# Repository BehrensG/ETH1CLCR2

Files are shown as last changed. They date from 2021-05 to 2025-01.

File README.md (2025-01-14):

<h1>ETH1CLCR2</h1>
LCR measurement card with Ethernet interface.

<h2>PCB Design</h2>

<p align="center">3D model rendition for PCB V1.0.</p>
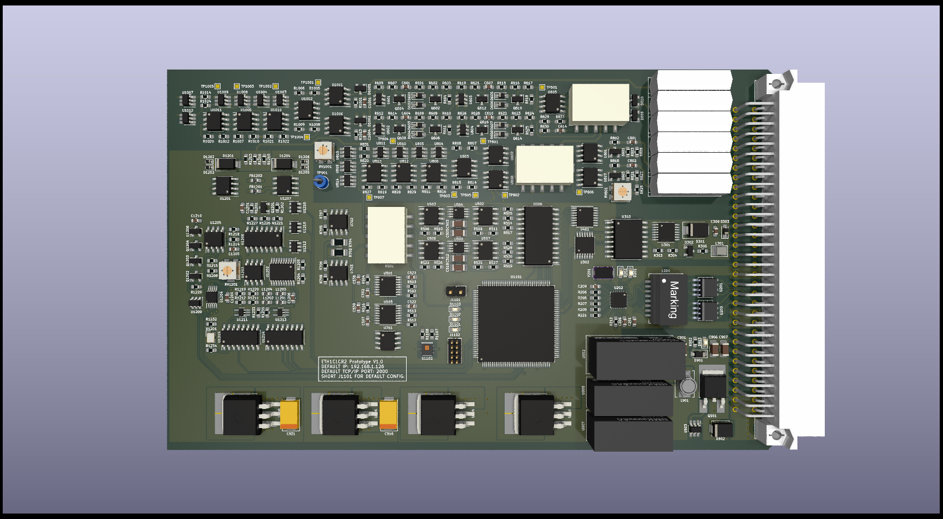
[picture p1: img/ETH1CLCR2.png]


<p align="center">Below are the images for the PCB V1.0. Mistake solved with botch wire.</p>

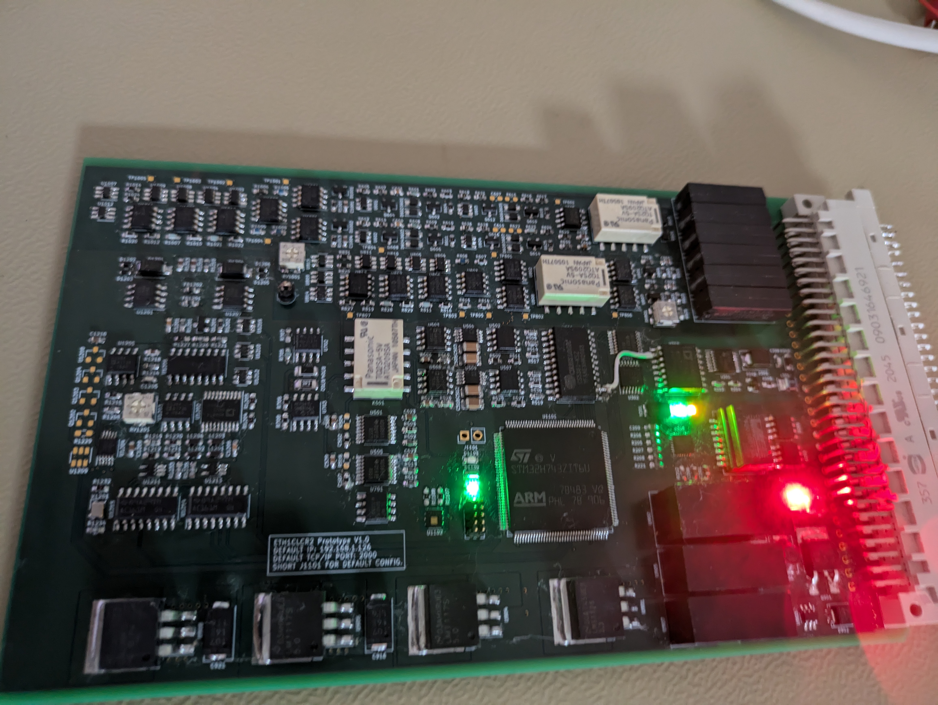
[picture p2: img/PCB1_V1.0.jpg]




<h2>Tests</h2>
Some test measurements perform on passive components. 

>[!NOTE]
>The components where measured directly, not in a circuit. The cards was not calibrated.

<table align="center">
    <tr>
        <th>Type</th>
        <th>Component</th>
        <th>Value</th>
        <th>Component Tolerance</th>
        <th>Measurement</th>
    </tr>
    <tr>
        <td>Resistor</td>
        <td>WS21R000FEK</td>
        <td>2 Ω</td>
        <td>1%</td>
        <td>2.2352 Ω</td>
    </tr>
    <tr>
        <td>Resistor</td>
        <td>SR1206JR-7W3R3L</td>
        <td>3.3 Ω</td>
        <td>5%</td>
        <td>3.8283 Ω</td>
    </tr>
    <tr>
        <td>Resistor</td>
        <td>PTF5610K000AYEK</td>
        <td>10 kΩ</td>
        <td>0.05%</td>
        <td>10.01509 kΩ</td>
    </tr>
    <tr>
        <td>Resistor</td>
        <td>RN732BTTD9002B25</td>
        <td>90 kΩ</td>
        <td>0.1%</td>
        <td>90.02021 kΩ</td>
    </tr>
    <tr>
        <td>Resistor</td>
        <td>ERA-8VRB1003V</td>
        <td>100 kΩ</td>
        <td>0.1%</td>
        <td>100.294 kΩ</td>
    </tr>
    <tr>
        <td>Resistor</td>
        <td>HHV-50FR-52-10M</td>
        <td>10 MegΩ</td>
        <td>1%</td>
        <td>10.490122 MegΩ</td>
    </tr>
    <tr>
        <td>Inductor</td>
        <td>AISR-01-104J</td>
        <td>100 mH</td>
        <td>5%</td>
        <td>102.6 mH</td>
    </tr>
    <tr>
        <td>Capacitor</td>
        <td>KP1830310061</td>
        <td>10 nF</td>
        <td>1%</td>
        <td>10.07 nF</td>
    </tr>
    <tr>
        <td>Capacitor</td>
        <td>F461BC104F400A</td>
        <td>100 nF</td>
        <td>1%</td>
        <td>106 nF</td>
    </tr>
    <tr>
        <td>Capacitor</td>
        <td>C315C101F3G5TA</td>
        <td>0.1 nF</td>
        <td>1%</td>
        <td>0.1071 nF</td>
    </tr>
    <tr>
        <td>Capacitor</td>
        <td>D83W4010M01H</td>
        <td>10 uF</td>
        <td>3%</td>
        <td>10.152 uF</td>
    </tr>
    <tr>
        <td>Capacitor</td>
        <td>MPK1839510401</td>
        <td>1 uF</td>
        <td>1%</td>
        <td>1.0695 uF</td>
    </tr>
    <tr>
        <td>Capacitor</td>
        <td>EST108M063AM3AA</td>
        <td>1 mF</td>
        <td>20%</td>
        <td>1.1 mF</td>
    </tr>
    <tr>
        <td>Capacitor</td>
        <td>F463AG102F2K0A</td>
        <td>1 nF</td>
        <td>1%</td>
        <td>1.0459 nF</td>
    </tr>
    <tr>
        <td>Capacitor</td>
        <td>MKP1839310251</td>
        <td>10 nF</td>
        <td>1%</td>
        <td>10.0974 nF</td>
    </tr>
    <tr>
        <td>Capacitor</td>
        <td>MKP1837410011</td>
        <td>100 nF</td>
        <td>1%</td>
        <td>101.457 nF</td>
    </tr>
    <tr>
        <td>Capacitor</td>
        <td>23PS222</td>
        <td>2.2 nF</td>
        <td>5%</td>
        <td>2.2161 nF</td>
    </tr>
</table>

<h2>NOTES</h2>
The ETH1CLCR2 PCB works, but I don't recommend using this design. The design has mistakes and could be made simpler and better.

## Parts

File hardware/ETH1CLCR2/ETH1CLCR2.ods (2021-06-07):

Id | Designator | Package | Quantity | Designation | Missing | Reference
1 | C1236,C1235,C1234,C1233,C536,C535,C534,C1232,C1231,C1226,C1230,C1229,C1228,C1227,C1225,C1224,C1223,C1222,C1221,C1220,C1219,C1218,C1217,C1216,C1215,C1214,C1213,C1212,C1211,C1203,C533,C532,C531,C530,C529,C528,C527,C526,C525,C524,C1121,C1120,C1119,C1118,C1117,C1116,C1115,C1114,C1113,C1112,C1111,C1110,C1109,C1108,C1107,C1105,C1019,C1018,C1015,C1014,C1013,C1012,C1011,C1016,C1010,C1017,C1009,C1008,C1007,C820,C819,C818,C813,C812,C817,C816,C815,C814,C822,C823,C811,C821,C810,C809,C808,C807,C624,C623,C622,C621,C620,C619,C618,C617,C616,C615,C612,C609,C606,C603,C523,C522,C521,C520,C308,C306,C304,C303,C301,C210,C207,C206,C205,C204,C202,C201 | C_0603_1608Metric_Pad1.08x0.95mm_HandSolder | 116 | 100n | 100
2 | C539,C538,C1210,C626,C625,C510,C1122,C1106,C1005,C1004,C1003,C1001,C805,C804,C802,C801,C704,C703,C701,C516,C514,C401,C307,C305,C302,C209,C203 | C_0603_1608Metric_Pad1.08x0.95mm_HandSolder | 27 | 1u
3 | C537,C1201,C509 | C_0603_1608Metric_Pad1.08x0.95mm_HandSolder | 3 | 10n
4 | R535,R534,R533,R532,R1230,R512,R1106,R1105,R1104,R812,R635,R627,R620,R613,R606,R513,R503,R502,R301,R220,R219,R218,R217,R213,R207 | R_0603_1608Metric_Pad0.98x0.95mm_HandSolder | 25 | 10k
5 | U1209,U1216,U1212,U1210,U604,U603,U602,U601 | SOT-23-6 | 8 | SN74LVC1T45DBV
6 | U1208 | SOT-23 | 1 | TL431DBZ | TL431IDBZR,215
7 | R1231,R1218,R1103,R1101 | R_0603_1608Metric_Pad0.98x0.95mm_HandSolder | 4 | 680 | 2
8 | R1229 | R_0603_1608Metric_Pad0.98x0.95mm_HandSolder | 1 | 51
9 | Q1204 | SOT-23 | 1 | DTC114E
10 | Q1203 | SOT-23 | 1 | DTA144E
11 | Q1202 | SOT-23 | 1 | 2SC3326B
12 | U808,U703,U1010,U1005,U1002,U812,U806,U803,U802 | SOIC-8_3.9x4.9mm_P1.27mm | 9 | MCP661-E/SN
13 | C613,C1006,C1002,C806,C803,C611,C610,C608,C607,C605,C602 | C_0603_1608Metric_Pad1.08x0.95mm_HandSolder | 11 | DNP
14 | R632,R631 | R_0603_1608Metric_Pad0.98x0.95mm_HandSolder | 2 | 2/.5%
15 | R1222,R1024,R1014,R831,R820,R302 | R_0603_1608Metric_Pad0.98x0.95mm_HandSolder | 6 | 1k | 1
16 | U906,U904 | TO-263-3_TabPin2 | 2 | LM1117SX-5.0/NOPB
17 | U1211 | SOT-353_SC-70-5_Handsoldering | 1 | 74AHC1G14
18 | C515,C513 | C_0805_2012Metric_Pad1.18x1.45mm_HandSolder | 2 | 22u
19 | U815,U814,U809,U1012,U1007 | SOT-23-6_Handsoldering | 5 | SN74LVC1T45DBV | 4 | 14.01.2022 | SN74LVC1T45MDCKREP
20 | TP901 | TestPoint_Loop_D2.60mm_Drill1.6mm_Beaded | 1 | TestPoint
21 | TP1005,TP1004,TP1003,TP1002,TP1001,TP807,TP806,TP805,TP804,TP803,TP802,TP801,TP601 | TestPoint_Pad_1.0x1.0mm | 13 | TestPoint
22 | D608,D607,D606,D605,D604,D603,D602,D601 | D_SOD-323_HandSoldering | 8 | BAS16J
23 | RV1201 | Potentiometer_Bourns_3314J_Vertical | 1 | 3314J-1-104E
24 | RV1001,RV801 | Potentiometer_Bourns_3314J_Vertical | 2 | 3314J-1-203E | 3314J-1-253E
25 | X1201 | IQXO-791 | 1 | 830208220601
26 | C921,C916 | CP_EIA-7343-20_Kemet-V_Pad2.25x2.55mm_HandSolder | 2 | T521V107M016ATE050 | T521V107M016ATE040
27 | U908 | TO-263-3_TabPin2 | 1 | LM2990SX-5.0
28 | U901 | TO-263-3_TabPin2 | 1 | LM1117SX-3.3/NOPB
29 | U902 | NCS3 | 1 | NCS3S1205SC
30 | Q1201 | SOT-23 | 1 | FDV301N | DMG301NU-13
31 | L1204,L1202,L1203,L1201 | L_0603_1608Metric_Pad1.05x0.95mm_HandSolder | 4 | CBMF1608T100K
32 | L901 | PM1608S | 1 | PM1608S-100M-RC
33 | U1215,U1214 | SOIC-16_3.9x9.9mm_P1.27mm | 2 | 74AC161
34 | U1213 | SOT-353_SC-70-5_Handsoldering | 1 | 74AUP1G79
35 | U1206 | SOIC-16_3.9x9.9mm_P1.27mm | 1 | DG409DY
36 | U1207,U1201 | SOIC-8_3.9x4.9mm_P1.27mm | 2 | LMH6639MA
37 | U1205,U1203 | SOIC-8_3.9x4.9mm_P1.27mm | 2 | AD8038ARZ
38 | U1204 | VSSOP-10_3x3mm_P0.5mm | 1 | DAC7811
39 | U509,U504 | MSOP-8_3x3mm_P0.65mm | 2 | AD8476_MSOP
40 | U508,U503 | SOIC-8_3.9x4.9mm_P1.27mm | 2 | OP1177AR
41 | U507,U502 | SOIC-8_3.9x4.9mm_P1.27mm | 2 | AD8656
42 | U506 | SOIC-24W_7.5x15.4mm_P1.27mm | 1 | CS5361 |  | 19.08.2021
43 | R1235,R1234,R1233,R1226 | R_0603_1608Metric_Pad0.98x0.95mm_HandSolder | 4 | 68
44 | R1202,R1232,R1110,R1109,R1108,R1107 | R_0603_1608Metric_Pad0.98x0.95mm_HandSolder | 6 | 4k7
45 | R1201,R1208,R529,R524,R515,R508,R901 | R_0603_1608Metric_Pad0.98x0.95mm_HandSolder | 7 | 100k
46 | R1216,R1213,R1210 | R_0603_1608Metric_Pad0.98x0.95mm_HandSolder | 3 | 150 | 2
47 | R1224,R1206,R1223,R1012,R819,R304 | R_0603_1608Metric_Pad0.98x0.95mm_HandSolder | 6 | 100
48 | R1217,R1203 | R_0603_1608Metric_Pad0.98x0.95mm_HandSolder | 2 | 680/.1%
49 | R1225,R1209 | R_0603_1608Metric_Pad0.98x0.95mm_HandSolder | 2 | 330/.1%
50 | R1227,R1215,R1220,R1212,R1211 | R_0603_1608Metric_Pad0.98x0.95mm_HandSolder | 5 | 200
51 | R1228,R212,R208,R206,R205 | R_0603_1608Metric_Pad0.98x0.95mm_HandSolder | 5 | 33 | 1
52 | R1221,R1214 | R_0603_1608Metric_Pad0.98x0.95mm_HandSolder | 2 | 220
53 | R1207 | R_0603_1608Metric_Pad0.98x0.95mm_HandSolder | 1 | 820
54 | R1219,R902 | R_0603_1608Metric_Pad0.98x0.95mm_HandSolder | 2 | 330
55 | R1205 | R_0603_1608Metric_Pad0.98x0.95mm_HandSolder | 1 | 2k
56 | R1204 | R_0603_1608Metric_Pad0.98x0.95mm_HandSolder | 1 | 6k8
57 | R810,R809 | R_0603_1608Metric_Pad0.98x0.95mm_HandSolder | 2 | 200/.1%
58 | R530,R517,R518,R501 | R_0603_1608Metric_Pad0.98x0.95mm_HandSolder | 4 | 634/.1%
59 | R528,R519,R514,R505 | R_0603_1608Metric_Pad0.98x0.95mm_HandSolder | 4 | 91/.1%
60 | R527,R526,R525,R522,R511,R509,R510,R506,R616 | R_0603_1608Metric_Pad0.98x0.95mm_HandSolder | 9 | 10k/.1%
61 | R523,R507 | R_0603_1608Metric_Pad0.98x0.95mm_HandSolder | 2 | 300
62 | R531,R628,R626,R621,R619,R614,R612,R607,R605 | R_0603_1608Metric_Pad0.98x0.95mm_HandSolder | 9 | 10K
63 | Q501,Q801,Q617,Q615,Q611,Q607,Q603 | SOT-23 | 7 | BC847 | 3
64 | K501,K801,K601 | SA | 3 | TQ2SA-5V
65 | FB1202,FB1201 | L_0603_1608Metric_Pad1.05x0.95mm_HandSolder | 2 | BLM18SP601SZ1D
66 | D1206,D1203,D1205,D1202 | D_SOD-523 | 4 | BZX584C5V6
67 | D1204,D1201 | D_SMA | 2 | BYG20J
68 | D501,D802,D611 | D_SOD-123 | 3 | 1N4148W
69 | C1205 | C_0603_1608Metric_Pad1.08x0.95mm_HandSolder | 1 | 3p3/COG
70 | C1209,C1204,C1202 | C_0603_1608Metric_Pad1.08x0.95mm_HandSolder | 3 | 4u7
71 | C1208,C1206 | C_0603_1608Metric_Pad1.08x0.95mm_HandSolder | 2 | 100p
72 | C1207 | C_0603_1608Metric_Pad1.08x0.95mm_HandSolder | 1 | 68p
73 | C901 | C_1206_3216Metric_Pad1.33x1.80mm_HandSolder | 1 | 4u7
74 | C519,C506,C508,C501 | C_0603_1608Metric_Pad1.08x0.95mm_HandSolder | 4 | 470p/COG
75 | C518,C512,C505,C503,C918,C917,C913,C912,C909,C908,C903,C902 | C_1206_3216Metric_Pad1.33x1.80mm_HandSolder | 12 | 10u
76 | C517,C504 | C_0603_1608Metric_Pad1.08x0.95mm_HandSolder | 2 | 2700p/COG
77 | C511 | C_1206_3216Metric_Pad1.33x1.80mm_HandSolder | 1 | 47u
78 | U1202 | TSSOP-20_4.4x6.5mm_P0.65mm | 1 | AD9834
79 | C907,C906 | C_1206_3216Metric_Pad1.33x1.80mm_HandSolder | 2 | 4u7/50V
80 | U605 | SOIC-8-1EP_3.9x4.9mm_P1.27mm_EP2.29x3mm | 1 | ADA4817-1ARDZ |  | 26.08.2021
81 | Y1101 | NX3225GD | 1 | NX3225GD-8MHZ |  | 05.11.2021
82 | Y201 | NX5032GA | 1 | NX5032GA-25.000M-LN-CD-1 |  | 12.08.2021
83 | U1103 | MSOP-8_3x3mm_P0.65mm | 1 | 24LC08B-E/MS
84 | U1102 | Texas_PWSON-N6 | 1 | HDC1080
85 | U1101 | TQFP-144_20x20mm_P0.5mm | 1 | STM32H743ZI
86 | U1011,U1006,U1001,U813,U807,U801 | SOIC-8_3.9x4.9mm_P1.27mm | 6 | MCP6L91T-E/SN
87 | U1009,U1008,U1004,U1003,U811,U810,U805,U804 | SOT-23-6_Handsoldering | 8 | SN74LVC1G3157DBVR |  | 25.06.2021
88 | U907 | NMK_DUAL | 1 | NMK2409SC
89 | U905 | NMK_SINGLE | 1 | NMK2409SAC
90 | U903 | SOT-23-6_Handsoldering | 1 | MAX5902
91 | U702 | SOIC-8_3.9x4.9mm_P1.27mm | 1 | TL431BCDE4
92 | U701 | SOIC-8_3.9x4.9mm_P1.27mm | 1 | REF5040ID
93 | U505,U501 | TSSOP-16_4.4x5mm_P0.65mm | 2 | ADS8681IPWR
94 | U401 | TSSOP-16_4.4x5mm_P0.65mm | 1 | ULN2003A
95 | U303 | SOIC-16W_7.5x10.3mm_P1.27mm | 1 | ADuM5402
96 | U302 | TSSOP-14_4.4x5mm_P0.65mm | 1 | TXB0104PW
97 | U301 | TSSOP-14_4.4x5mm_P0.65mm | 1 | 74AC125
98 | U203,U201 | SO8E | 2 | LC03-3.3
99 | U202 | QFN-24-1EP_4x4mm_P0.5mm_EP2.6x2.6mm_ThermalVias | 1 | LAN8742A
100 | R1102 | R_0603_1608Metric_Pad0.98x0.95mm_HandSolder | 1 | 560
101 | R1023,R1011,R830,R817 | R_0603_1608Metric_Pad0.98x0.95mm_HandSolder | 4 | 18k/.1%
102 | R1022,R1018,R1017,R1010,R1004,R1003,R829,R823,R822,R816,R805,R804 | R_0603_1608Metric_Pad0.98x0.95mm_HandSolder | 12 | 2k/.1%
103 | R1021,R1007,R828,R811,R623 | R_0603_1608Metric_Pad0.98x0.95mm_HandSolder | 5 | 100k/.1%
104 | R1020,R827,R708,R706 | R_0603_1608Metric_Pad0.98x0.95mm_HandSolder | 4 | 3k3/.1%
105 | R1019,R825 | R_0603_1608Metric_Pad0.98x0.95mm_HandSolder | 2 | 47k/.1%
106 | R1016,R824,R813,R801,R634,R622,R615 | R_0603_1608Metric_Pad0.98x0.95mm_HandSolder | 7 | DNP
107 | R1015,R1002,R821,R803,R625,R624,R618,R617,R611,R610,R604,R603 | R_0603_1608Metric_Pad0.98x0.95mm_HandSolder | 12 | 1Meg
108 | R1013,R1001,R818,R802,R629,R602 | R_0603_1608Metric_Pad0.98x0.95mm_HandSolder | 6 | 100/.1%
109 | R1009,R1008,R1006,R1005,R815,R814,R808,R807,R609 | R_0603_1608Metric_Pad0.98x0.95mm_HandSolder | 9 | 1k/.1% | 4
110 | R826,R806 | R_0603_1608Metric_Pad0.98x0.95mm_HandSolder | 2 | 1k8/.1%
111 | R707 | R_0603_1608Metric_Pad0.98x0.95mm_HandSolder | 1 | 1k1/.1%
112 | R705 | R_0603_1608Metric_Pad0.98x0.95mm_HandSolder | 1 | 220/.1%
113 | R704 | R_1206_3216Metric_Pad1.30x1.75mm_HandSolder | 1 | 33/.5W
114 | R703 | R_0603_1608Metric_Pad0.98x0.95mm_HandSolder | 1 | 10
115 | R702 | R_1206_3216Metric_Pad1.30x1.75mm_HandSolder | 1 | 3R3/.5W
116 | R701,R521,R520 | R_0603_1608Metric_Pad0.98x0.95mm_HandSolder | 3 | 0R22
117 | R633,R516,R504 | R_0603_1608Metric_Pad0.98x0.95mm_HandSolder | 3 | 0
118 | R630 | R_0603_1608Metric_Pad0.98x0.95mm_HandSolder | 1 | 47/.1%
119 | R608,R601 | R_0603_1608Metric_Pad0.98x0.95mm_HandSolder | 2 | 33/.1%
120 | R306 | R_0603_1608Metric_Pad0.98x0.95mm_HandSolder | 1 | 51R1
121 | R305 | R_0603_1608Metric_Pad0.98x0.95mm_HandSolder | 1 | 47
122 | R303 | R_0603_1608Metric_Pad0.98x0.95mm_HandSolder | 1 | 14k7
123 | R221 | R_0603_1608Metric_Pad0.98x0.95mm_HandSolder | 1 | 1k5
124 | R216 | R_1206_3216Metric_Pad1.30x1.75mm_HandSolder | 1 | 1M/1kV
125 | R215,R214 | R_0603_1608Metric_Pad0.98x0.95mm_HandSolder | 2 | 270
126 | R211,R210 | R_0603_1608Metric_Pad0.98x0.95mm_HandSolder | 2 | 75/1%
127 | R209 | R_0603_1608Metric_Pad0.98x0.95mm_HandSolder | 1 | 12k1
128 | R204,R203,R202,R201 | R_0603_1608Metric_Pad0.98x0.95mm_HandSolder | 4 | 49R9
129 | Q901 | TO-252-2_Rectifier | 1 | IRFR5410
130 | Q616,Q612,Q608,Q604 | SOT-23 | 4 | BC857
131 | Q614,Q613,Q610,Q609,Q606,Q605,Q602,Q601 | SOT-23 | 8 | MMBFJ309LT1G
132 | L301 | CW252016 | 1 | CW252016-R33G
133 | L201 | 749010012A | 1 | 749010012A
134 | K405,K404,K403,K402,K401 | HE360_x-5050462-8 | 6 | HE3621A0510
135 | J1102 | PinHeader_2x05_P1.27mm_Vertical | 1 | 20021111-00010T4LF
136 | J1101 | PinHeader_1x02_P2.54mm_Vertical | 1 | Conn_02x01
137 | J401 | Socket_DIN41612-CaseC1-AC-Male-64Pin-2rows | 1 | C64AC
138 | FB1101,FB201 | L_0805_2012Metric_Pad1.15x1.40mm_HandSolder | 2 | 742792031
139 | FB1001,FB801 | L_0603_1608Metric_Pad1.05x0.95mm_HandSolder | 2 | BLM18TG102TN1D
140 | F901 | Fuse_SMD2920 | 1 | MF-LSMF185/33X | MF-LSMF260X-2
141 | D1103 | LED_0603_1608Metric_Pad1.05x0.95mm_HandSolder | 1 | BLUE
142 | D1102,D202 | LED_0603_1608Metric_Pad1.05x0.95mm_HandSolder | 2 | GREEN
143 | D1101,D903 | LED_0603_1608Metric_Pad1.05x0.95mm_HandSolder | 2 | RED
144 | D1002,D1001,D803,D801,D610,D609 | SOT-23 | 6 | BAV199
145 | D902 | DO_214AA_REV | 1 | SM6T30AY
146 | D901 | D_SOD-123 | 1 | MMSZ5249B
147 | D303 | D_SOD-323_HandSoldering | 1 | SD36C-01FTG | PJSD36CW-AU_R1_000A1
148 | D302 | SOT-23 | 1 | BAV99
149 | D301 | D_SMB | 1 | SMBJ5.0A
150 | D201 | LED_0603_1608Metric_Pad1.05x0.95mm_HandSolder | 1 | YELLOW
151 | C1104,C1103 | C_0603_1608Metric_Pad1.08x0.95mm_HandSolder | 2 | 2u2
152 | C1102,C1101,C214,C213 | C_0603_1608Metric_Pad1.08x0.95mm_HandSolder | 4 | 8p
153 | C920,C915,C911,C905 | C_1206_3216Metric_Pad1.33x1.80mm_HandSolder | 4 | 100n
154 | C919,C914,C910,C904 | C_1206_3216Metric_Pad1.33x1.80mm_HandSolder | 4 | 1u
155 | C705,C702 | C_0805_2012Metric_Pad1.18x1.45mm_HandSolder | 2 | 10u
156 | C614,C208 | C_0603_1608Metric_Pad1.08x0.95mm_HandSolder | 2 | 470p
157 | C604,C601 | C_0603_1608Metric_Pad1.08x0.95mm_HandSolder | 2 | 4n7
158 | C507,C502 | C_0603_1608Metric_Pad1.08x0.95mm_HandSolder | 2 | 330p
159 | C309 | C_0603_1608Metric_Pad1.08x0.95mm_HandSolder | 1 | 47p
160 | C212,C211 | C_1206_3216Metric_Pad1.33x1.80mm_HandSolder | 2 | 1n/1kV

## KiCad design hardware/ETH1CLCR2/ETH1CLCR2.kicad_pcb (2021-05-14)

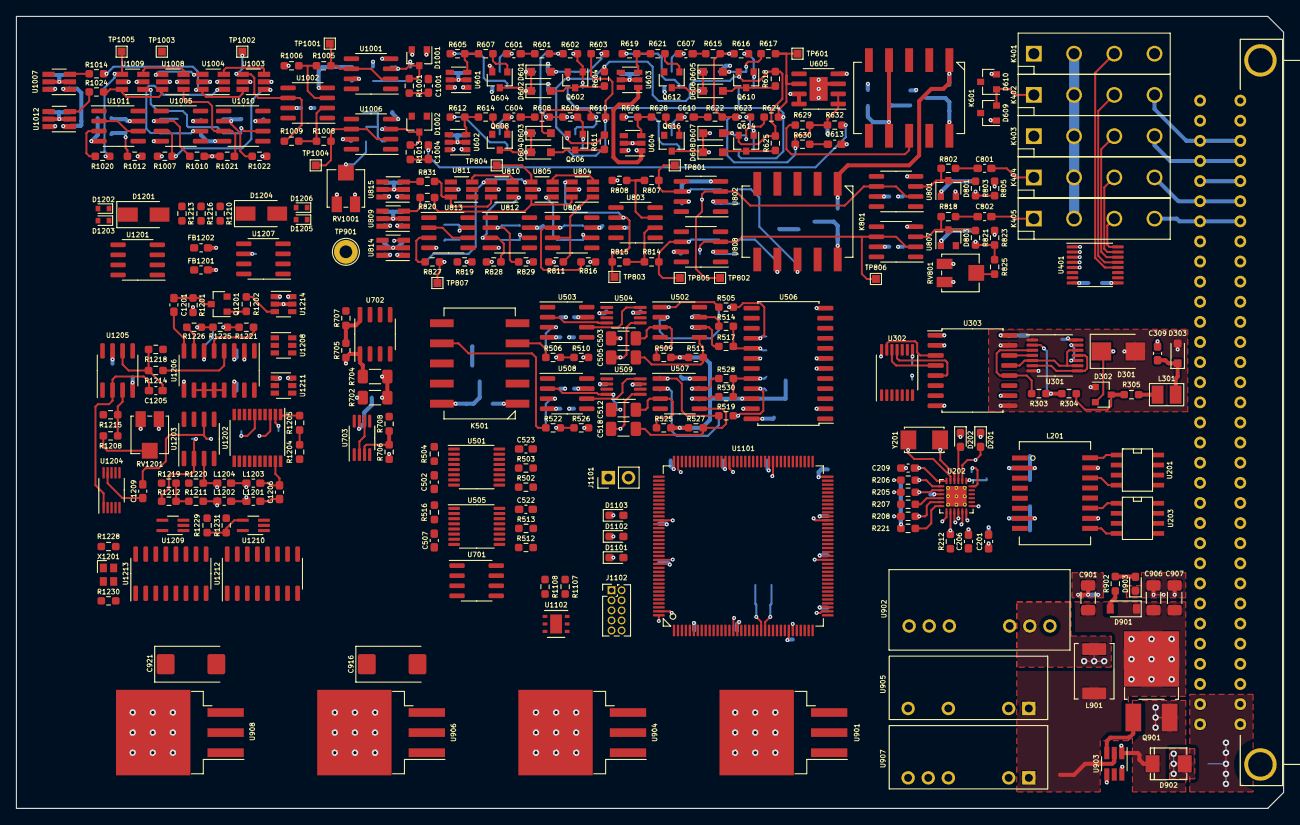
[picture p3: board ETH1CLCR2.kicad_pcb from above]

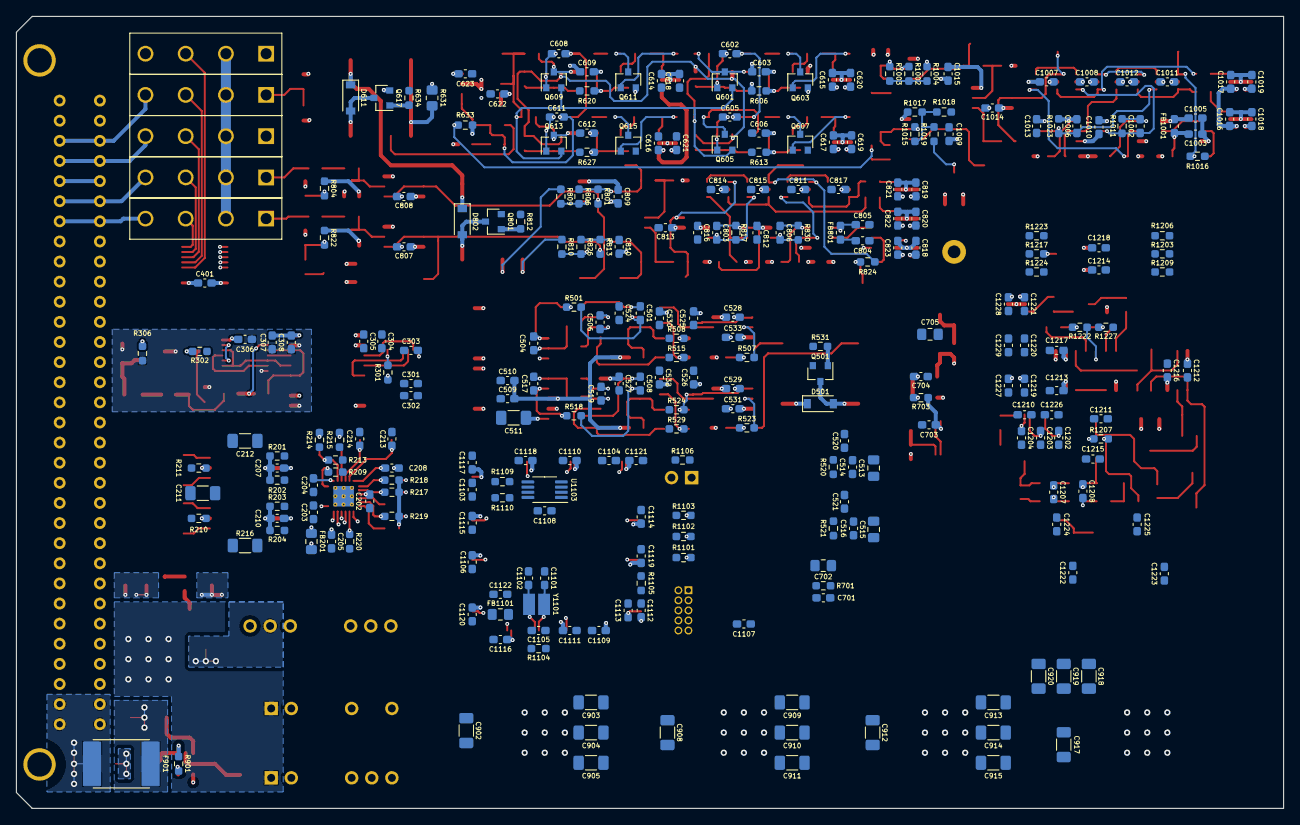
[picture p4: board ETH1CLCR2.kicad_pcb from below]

Board: 6 copper layers, 160.0 x 100.0 mm, 573 parts (268 on the bottom side), 354 nets.

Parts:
C201, C202, C204, C205, C206, C207, C210, C301, C303, C304, C306, C308, C520, C521, C522, C523, C524, C525, C526, C527, C528, C529, C530, C531, C532, C533, C603, C606, C609, C612, C614, C615, C616, C617, C618, C619, C620, C621, C622, C623, C807, C808, C809, C810, C811, C812, C813, C814, C815, C816, C817, C818, C819, C820, C821, C822, C823, C1007, C1008, C1009, C1010, C1011, C1012, C1013, C1014, C1015, C1016, C1017, C1018, C1019, C1105, C1107, C1108, C1109, C1110, C1111, C1112, C1113, C1114, C1115, C1116, C1117, C1118, C1119, C1120, C1121, C1203, C1210, C1211, C1212, C1213, C1214, C1215, C1216, C1217, C1218, C1219, C1220, C1221, C1222, C1223, C1224, C1225, C1226, C1227, C1228, C1229: 100n; C_0603_1608Metric_Pad1.08x0.95mm_HandSolder
C203, C209, C302, C305, C307, C401, C510, C514, C516, C701, C703, C704, C801, C802, C804, C805, C1001, C1003, C1004, C1005, C1106, C1122: 1u; C_0603_1608Metric_Pad1.08x0.95mm_HandSolder
C208, C613: 470p; C_0603_1608Metric_Pad1.08x0.95mm_HandSolder
C211, C212: 1n/1kV; C_1206_3216Metric_Pad1.33x1.80mm_HandSolder
C213, C214, C1101, C1102: 8p; C_0603_1608Metric_Pad1.08x0.95mm_HandSolder
C309: 47p; C_0603_1608Metric_Pad1.08x0.95mm_HandSolder
C501, C506, C508, C519: 470p/COG; C_0603_1608Metric_Pad1.08x0.95mm_HandSolder
C502, C507: 330p; C_0603_1608Metric_Pad1.08x0.95mm_HandSolder
C503, C505, C512, C518, C902, C903, C908, C909, C912, C913, C917, C918: 10u; C_1206_3216Metric_Pad1.33x1.80mm_HandSolder
C504, C517: 2700p/COG; C_0603_1608Metric_Pad1.08x0.95mm_HandSolder
C509, C1201: 10n; C_0603_1608Metric_Pad1.08x0.95mm_HandSolder
C511: 47u; C_1206_3216Metric_Pad1.33x1.80mm_HandSolder
C513, C515: 22u; C_0805_2012Metric_Pad1.18x1.45mm_HandSolder
C601, C604: 4n7; C_0603_1608Metric_Pad1.08x0.95mm_HandSolder
C602, C605, C607, C608, C610, C611, C803, C806, C1002, C1006: DNP; C_0603_1608Metric_Pad1.08x0.95mm_HandSolder
C702, C705: 10u; C_0805_2012Metric_Pad1.18x1.45mm_HandSolder
C901: 4u7; C_1206_3216Metric_Pad1.33x1.80mm_HandSolder
C904, C910, C914, C919: 1u; C_1206_3216Metric_Pad1.33x1.80mm_HandSolder
C905, C911, C915, C920: 100n; C_1206_3216Metric_Pad1.33x1.80mm_HandSolder
C906, C907: 4u7/50V; C_1206_3216Metric_Pad1.33x1.80mm_HandSolder
C916, C921: T521V107M016ATE050; CP_EIA-7343-20_Kemet-V_Pad2.25x2.55mm_HandSolder
C1103, C1104: 2u2; C_0603_1608Metric_Pad1.08x0.95mm_HandSolder
C1202, C1204, C1209: 4u7; C_0603_1608Metric_Pad1.08x0.95mm_HandSolder
C1205: 3p3/COG; C_0603_1608Metric_Pad1.08x0.95mm_HandSolder
C1206, C1208: 100p; C_0603_1608Metric_Pad1.08x0.95mm_HandSolder
C1207: 68p; C_0603_1608Metric_Pad1.08x0.95mm_HandSolder
D201: YELLOW; LED_0603_1608Metric_Pad1.05x0.95mm_HandSolder
D202, D1102: GREEN; LED_0603_1608Metric_Pad1.05x0.95mm_HandSolder
D301: SMBJ5.0A; D_SMB
D302: BAV99; SOT-23
D303: SD36C-01FTG; D_SOD-323_HandSoldering
D501, D611, D802: 1N4148W; D_SOD-123
D601, D602, D603, D604, D605, D606, D607, D608: BAS16J; D_SOD-323_HandSoldering
D609, D610, D801, D803, D1001, D1002: BAV199; SOT-23
D901: MMSZ5249B; D_SOD-123
D902: SM6T30AY; DO_214AA_REV
D903, D1101: RED; LED_0603_1608Metric_Pad1.05x0.95mm_HandSolder
D1103: BLUE; LED_0603_1608Metric_Pad1.05x0.95mm_HandSolder
D1201, D1204: BYG20J; D_SMA
D1202, D1203, D1205, D1206: BZX584C5V6; D_SOD-523
F901: MF-LSMF185/33X; Fuse_SMD2920
FB201, FB1101: 742792031; L_0805_2012Metric_Pad1.15x1.40mm_HandSolder
FB801, FB1001: BLM18TG102TN1D; L_0603_1608Metric_Pad1.05x0.95mm_HandSolder
FB1201, FB1202: BLM18SP601SZ1D; L_0603_1608Metric_Pad1.05x0.95mm_HandSolder
J401: C64AC; Socket_DIN41612-CaseC1-AC-Male-64Pin-2rows
J1101: Conn_02x01; PinHeader_1x02_P2.54mm_Vertical
J1102: 20021111-00010T4LF; PinHeader_2x05_P1.27mm_Vertical
K401, K402, K403, K404, K405: HE3621A0510; HE360_x-5050462-8
K501, K601, K801: TQ2SA-5V; SA
L201: 749010012A
L301: CW252016-R33G; CW252016
L901: PM1608S-100M-RC; PM1608S
L1201, L1202, L1203, L1204: CBMF1608T100K; L_0603_1608Metric_Pad1.05x0.95mm_HandSolder
Q501, Q603, Q607, Q611, Q615, Q617, Q801: BC847; SOT-23
Q601, Q602, Q605, Q606, Q609, Q610, Q613, Q614: MMBFJ309LT1G; SOT-23
Q604, Q608, Q612, Q616: BC857; SOT-23
Q901: IRFR5410; TO-252-2_Rectifier
Q1201: FDV301N; SOT-23
R201, R202, R203, R204: 49R9; R_0603_1608Metric_Pad0.98x0.95mm_HandSolder
R205, R206, R208, R212, R1227: 33; R_0603_1608Metric_Pad0.98x0.95mm_HandSolder
R207, R213, R217, R218, R219, R220, R301, R502, R503, R509, R511, R512, R513, R525, R527, R606, R613, R620, R627, R634, R812, R1104, R1105, R1106: 10k; R_0603_1608Metric_Pad0.98x0.95mm_HandSolder
R209: 12k1; R_0603_1608Metric_Pad0.98x0.95mm_HandSolder
R210, R211: 75/1%; R_0603_1608Metric_Pad0.98x0.95mm_HandSolder
R214, R215: 270; R_0603_1608Metric_Pad0.98x0.95mm_HandSolder
R216: 1M/1kV; R_1206_3216Metric_Pad1.30x1.75mm_HandSolder
R221: 1k5; R_0603_1608Metric_Pad0.98x0.95mm_HandSolder
R302, R820, R831, R1014, R1024, R1228: 1k; R_0603_1608Metric_Pad0.98x0.95mm_HandSolder
R303: 14k7; R_0603_1608Metric_Pad0.98x0.95mm_HandSolder
R304, R819, R1012, R1206, R1222, R1223: 100; R_0603_1608Metric_Pad0.98x0.95mm_HandSolder
R305: 47; R_0603_1608Metric_Pad0.98x0.95mm_HandSolder
R306: 51R1; R_0603_1608Metric_Pad0.98x0.95mm_HandSolder
R501, R517, R518, R530: 634; R_0603_1608Metric_Pad0.98x0.95mm_HandSolder
R504, R516, R632: 0; R_0603_1608Metric_Pad0.98x0.95mm_HandSolder
R505, R514, R519, R528: 91; R_0603_1608Metric_Pad0.98x0.95mm_HandSolder
R506, R510, R522, R526, R616: 10k/.1%; R_0603_1608Metric_Pad0.98x0.95mm_HandSolder
R507, R523: 300; R_0603_1608Metric_Pad0.98x0.95mm_HandSolder
R508, R515, R524, R529, R901, R1201, R1208: 100k; R_0603_1608Metric_Pad0.98x0.95mm_HandSolder
R520, R521, R701: 0R22; R_0603_1608Metric_Pad0.98x0.95mm_HandSolder
R531, R605, R607, R612, R614, R619, R621, R626, R628: 10K; R_0603_1608Metric_Pad0.98x0.95mm_HandSolder
R601, R608: 33/.1%; R_0603_1608Metric_Pad0.98x0.95mm_HandSolder
R602, R629, R802, R818, R1001, R1013: 100/.1%; R_0603_1608Metric_Pad0.98x0.95mm_HandSolder
R603, R604, R610, R611, R617, R618, R624, R625, R803, R821, R1002, R1015: 1Meg; R_0603_1608Metric_Pad0.98x0.95mm_HandSolder
R609, R807, R808, R814, R815, R1005, R1006, R1008, R1009: 1k/.1%; R_0603_1608Metric_Pad0.98x0.95mm_HandSolder
R615, R622, R633, R801, R813, R824, R1016: DNP; R_0603_1608Metric_Pad0.98x0.95mm_HandSolder
R623, R811, R828, R1007, R1021: 100k/.1%; R_0603_1608Metric_Pad0.98x0.95mm_HandSolder
R630: 47/.1%; R_0603_1608Metric_Pad0.98x0.95mm_HandSolder
R631: 0R1; R_0805_2012Metric_Pad1.20x1.40mm_HandSolder
R702: 3R3/.5W; R_1206_3216Metric_Pad1.30x1.75mm_HandSolder
R703: 10; R_0603_1608Metric_Pad0.98x0.95mm_HandSolder
R704: 33/.5W; R_1206_3216Metric_Pad1.30x1.75mm_HandSolder
R705: 220/.1%; R_0603_1608Metric_Pad0.98x0.95mm_HandSolder
R706, R708, R827, R1020: 3k3/.1%; R_0603_1608Metric_Pad0.98x0.95mm_HandSolder
R707: 1k1/.1%; R_0603_1608Metric_Pad0.98x0.95mm_HandSolder
R804, R805, R816, R822, R823, R829, R1003, R1004, R1010, R1017, R1018, R1022: 2k/.1%; R_0603_1608Metric_Pad0.98x0.95mm_HandSolder
R806, R826: 1k8/.1%; R_0603_1608Metric_Pad0.98x0.95mm_HandSolder
R809, R810: 200/.1%; R_0603_1608Metric_Pad0.98x0.95mm_HandSolder
R817, R830, R1011, R1023: 18k/.1%; R_0603_1608Metric_Pad0.98x0.95mm_HandSolder
R825, R1019: 47k/.1%; R_0603_1608Metric_Pad0.98x0.95mm_HandSolder
R902, R1209, R1219, R1224: 330; R_0603_1608Metric_Pad0.98x0.95mm_HandSolder
R1101, R1103, R1203, R1217, R1218: 680; R_0603_1608Metric_Pad0.98x0.95mm_HandSolder
R1102: 560; R_0603_1608Metric_Pad0.98x0.95mm_HandSolder
R1107, R1108, R1109, R1110, R1202: 4k7; R_0603_1608Metric_Pad0.98x0.95mm_HandSolder
R1204: 6k8; R_0603_1608Metric_Pad0.98x0.95mm_HandSolder
R1205: 2k; R_0603_1608Metric_Pad0.98x0.95mm_HandSolder
R1207: 820; R_0603_1608Metric_Pad0.98x0.95mm_HandSolder
R1210, R1213, R1216: 150; R_0603_1608Metric_Pad0.98x0.95mm_HandSolder
R1211, R1212, R1215, R1220, R1226: 200; R_0603_1608Metric_Pad0.98x0.95mm_HandSolder
R1214, R1221: 220; R_0603_1608Metric_Pad0.98x0.95mm_HandSolder
R1225, R1229, R1230, R1231: 68; R_0603_1608Metric_Pad0.98x0.95mm_HandSolder
RV801, RV1001: 3314J-1-203E; Potentiometer_Bourns_3314J_Vertical
RV1201: 3314J-1-104E; Potentiometer_Bourns_3314J_Vertical
TP601, TP801, TP802, TP803, TP804, TP805, TP806, TP807, TP1001, TP1002, TP1003, TP1004, TP1005: TestPoint; TestPoint_Pad_1.0x1.0mm
TP901: TestPoint; TestPoint_Loop_D2.60mm_Drill1.6mm_Beaded
U201, U203: LC03-3.3; SO8E
U202: LAN8742A; QFN-24-1EP_4x4mm_P0.5mm_EP2.6x2.6mm_ThermalVias
U301: 74AC125; TSSOP-14_4.4x5mm_P0.65mm
U302: TXB0104PW; TSSOP-14_4.4x5mm_P0.65mm
U303: ADuM5402; SOIC-16W_7.5x10.3mm_P1.27mm
U401: ULN2003A; TSSOP-16_4.4x5mm_P0.65mm
U501, U505: ADS8681PWR; TSSOP-16_4.4x5mm_P0.65mm
U502, U507: AD8656; SOIC-8_3.9x4.9mm_P1.27mm
U503, U508: OP1177AR; SOIC-8_3.9x4.9mm_P1.27mm
U504, U509: AD8476_MSOP; MSOP-8_3x3mm_P0.65mm
U506: CS5361; SOIC-24W_7.5x15.4mm_P1.27mm
U601, U602, U603, U604, U1208, U1211, U1214: SN74LVC1T45DBV; SOT-23-6
U605: ADA4817-1ARDZ; SOIC-8-1EP_3.9x4.9mm_P1.27mm_EP2.29x3mm
U701: REF5040ID; SOIC-8_3.9x4.9mm_P1.27mm
U702: TL431BCDE4; SOIC-8_3.9x4.9mm_P1.27mm
U703: MCP6L91RT-EMS; MSOP-8_3x3mm_P0.65mm
U801, U807, U813, U1001, U1006, U1011: MCP6L91RT-ESN; SOIC-8_3.9x4.9mm_P1.27mm
U802, U803, U806, U808, U812, U1002, U1005, U1010: MCP661; SOIC-8_3.9x4.9mm_P1.27mm
U804, U805, U810, U811, U1003, U1004, U1008, U1009: SN74LVC1G3157; SOT-23-6_Handsoldering
U809, U814, U815, U1007, U1012: SN74LVC1T45DBV; SOT-23-6_Handsoldering
U901: TLV1117-33; TO-263-3_TabPin2
U902: NCS3S1205SC; NCS3
U903: MAX5902; SOT-23-6_Handsoldering
U904, U906: TLV1117-50; TO-263-3_TabPin2
U905: NMK2409SAC; NMK_SINGLE
U907: NMK2409SC; NMK_DUAL
U908: LM2990SX-5.0; TO-263-3_TabPin2
U1101: STM32H743ZI; TQFP-144_20x20mm_P0.5mm
U1102: HDC1080; Texas_PWSON-N6
U1103: 24LC08B-E/MS; MSOP-8_3x3mm_P0.65mm
U1201, U1207: LMH6639; SOIC-8_3.9x4.9mm_P1.27mm
U1202: AD9834; TSSOP-20_4.4x6.5mm_P0.65mm
U1203, U1205: AD8038; SOIC-8_3.9x4.9mm_P1.27mm
U1204: DAC7811; VSSOP-10_3x3mm_P0.5mm
U1206: DG409; SOIC-16_3.9x9.9mm_P1.27mm
U1209: 74AHC1G14; SOT-353_SC-70-5_Handsoldering
U1210: 74AUP1G79; SOT-353_SC-70-5_Handsoldering
U1212, U1213: 74AC161; SOIC-16_3.9x9.9mm_P1.27mm
X1201: 830208220601; IQXO-791
Y201: NX5032GA-25.000M-LN-CD-1; NX5032GA
Y1101: NX3225GD-8MHZ; NX3225GD

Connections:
+1V5: R808.1, R811.2, R816.2, R828.2, R829.2, R1006.1, R1007.2, R1010.2, R1021.2, R1022.2, U703.2, U703.6
+3.3VP: C705.1, R704.1, R705.1, R706.1, R805.1, R823.1, R1004.1, R1018.1, RV801.1, RV1001.1, U702.1
+3V3: C201.1, C202.1, C301.1, C302.1, C522.1, C523.1, C618.1, C619.1, C620.1, C621.1, C818.1, C819.1, C820.1, C903.1, C904.1, C905.1, C1018.1, C1019.1, C1106.1, C1107.1, C1108.1, C1109.1, C1110.1, C1111.1, C1112.1, C1113.1, C1114.1, C1115.1, C1116.1, C1117.1, C1118.1, C1119.1, C1120.1, C1121.1, C1222.1, C1223.1, C1224.1, C1225.1, C1226.1, C1227.1, C1228.1, C1229.1, D1101.2, D1102.2, D1103.2, FB201.2, FB1101.2, J1102.1, R217.1, R218.1, R219.1, R220.1, R221.1, R301.1, R502.1, R503.1, R512.1, R513.1, R702.1, R1104.1, R1106.2, R1107.1, R1108.1, R1109.1, R1110.1, R1228.1, U202.9, U302.1, U501.16, U505.16, U506.2, U506.6, U506.8, U506.12, U601.6, U602.6, U603.6, U604.6, U809.6, U814.6, U815.6, U901.2, U1007.6, U1012.6, U1101.6, U1101.17, U1101.30, U1101.39, U1101.52, U1101.62, U1101.72, U1101.84, U1101.95, U1101.108, U1101.121, U1101.131, U1101.143, U1101.144, U1102.5, U1103.8, U1202.5, U1204.8, U1208.6, U1209.5, U1210.5, U1211.6, U1212.1, U1212.7, U1212.10, U1212.16, U1213.1, U1213.3, U1213.6, U1213.7, U1213.16, U1214.6, X1201.4
+4V: R701.1, U501.4, U505.4, U701.6
+5V: C303.1, C304.1, C305.1, C401.1, C520.1, C521.1, C614.1, C615.1, C616.1, C617.1, C821.1, C822.1, C823.1, C909.1, C910.1, C911.1, C1016.1, C1017.1, C1219.1, C1220.1, C1221.1, D501.1, D611.1, D802.1, K401.2, K402.2, K403.2, K404.2, K405.2, K501.1, K601.1, K801.1, U302.14, U303.1, U401.9, U501.2, U505.2, U506.19, U601.1, U602.1, U603.1, U604.1, U701.2, U809.1, U814.1, U815.1, U904.2, U1007.1, U1012.1, U1208.1, U1211.1, U1214.1
+5VA: C524.1, C525.1, C526.1, C527.1, C528.1, C529.1, C622.1, C807.1, C808.1, C809.1, C810.1, C811.1, C812.1, C813.1, C814.1, C815.1, C816.1, C817.1, C913.1, C914.1, C915.1, C916.1, C1007.1, C1008.1, C1009.1, C1010.1, C1011.1, C1012.1, C1013.1, C1014.1, C1015.1, C1210.1, C1211.1, C1212.1, C1213.1, C1214.1, D801.2, D803.2, D1001.2, D1002.2, D1201.1, D1202.1, D1203.1, FB1201.1, Q604.2, Q608.2, Q612.2, Q616.2, R819.2, R1012.2, R1201.1, RV1201.1, U502.8, U503.7, U504.2, U507.8, U508.7, U509.2, U605.7, U605.8, U801.7, U802.7, U803.7, U804.5, U805.5, U806.7, U807.7, U808.7, U810.5, U811.5, U812.7, U906.2, U1001.7, U1002.7, U1003.5, U1004.5, U1005.7, U1006.7, U1008.5, U1009.5, U1010.7, U1201.8, U1202.4, U1203.7, U1205.7, U1206.2, U1206.14, U1207.8
+5V_TRIG: C306.1, C307.1, C308.1, R302.1, U301.14, U303.10, U303.16
+24V: F901.2, J401.A31, J401.A32, J401.C31, J401.C32
-5VA: C530.1, C531.1, C532.1, C533.1, C623.1, C918.2, C919.2, C920.2, C921.2, C1215.1, C1216.1, C1217.1, C1218.1, D1204.2, D1205.2, D1206.2, FB1202.1, R606.2, R613.2, R620.2, R627.2, RV1201.3, U503.4, U504.7, U508.4, U509.7, U605.4, U908.3, U1203.4, U1205.4, U1206.3
/ADC/ADC1_IIN: K501.2, R504.2
/ADC/ADC1_MISO: R513.2, U505.13, U1101.112
/ADC/ADC1_MOSI: U501.10, U1101.113
/ADC/ADC1_RVS1: U501.15, U1101.114
/ADC/ADC1_RVS2: U505.15, U1101.115
/ADC/ADC1_SCLK: U501.12, U505.12, U1101.111
/ADC/ADC1_VIN: K501.9, R516.2
/ADC/ADC1_~CS: U501.11, U505.11, U1101.110
/ADC/ADC2_IIN: K501.4, R506.2
/ADC/ADC2_VIN: K501.7, R522.2
/ADC/ADC_IIN: K501.3, U1011.2, U1011.6
/ADC/ADC_VIN: K501.8, U813.2, U813.6
/ADC/CAP1: R520.1, U501.6
/ADC/CAP2: R521.1, U505.6
/ADC/DDS_CLK: R1231.1, U506.5
/ADC/VQ: C509.1, C510.1, R509.2, R511.2, R525.2, R527.2, U506.22
/Connector/A: J401.A2, J401.C2, K401.4
/Connector/B: J401.A3, J401.C3, K402.4
/Connector/C: J401.A4, J401.C4, K403.4
/Connector/CXN_REL1: U401.5, U1101.122
/Connector/CXN_REL2: U401.4, U1101.119
/Connector/CXN_REL3: U401.3, U1101.118
/Connector/CXN_REL4: U401.2, U1101.117
/Connector/CXN_REL5: U401.1, U1101.116
/Connector/D: J401.A5, J401.C5
/Connector/E: J401.A6, J401.C6, K404.4
/Connector/EXT_TRIG: C309.1, D303.1, J401.A16, L301.1
/Connector/F: J401.A7, J401.C7, K405.4
/Connector/H_CUR: K401.1, R1210.1, R1213.1, R1216.1
/Connector/H_POT: C801.2, K404.1
/Connector/L_CUR: D609.2, D610.1, K402.1, K601.3
/Connector/L_POT: C802.2, K405.1
/Connector/RX+: J401.A20, U203.8
/Connector/RX-: J401.A21, U203.5
/Connector/TX+: J401.C20, U201.8
/Connector/TX-: J401.C21, U201.5
/Current Diff Amp/CUR_IN: C1001.2, Q602.2, Q606.2, Q610.2, Q614.2, R604.1, R611.1, R618.1, R625.1
/Current Diff Amp/CUR_ZERO: C1004.2, R632.1, R633.1
/Current Diff Amp/IDIFF0: U1012.4, U1101.139
/Current Diff Amp/IDIFF1: U1007.4, U1101.140
/DDS/A0: U1206.1, U1208.3
/DDS/A1: U1206.16, U1211.3
/DDS/DDS_CS: U1101.73, U1202.15
/DDS/DDS_SCLK: U1101.74, U1202.14
/DDS/DDS_SDATA: U1101.76, U1202.13
/DDS/LPF: R1202.2, U1214.3
/DDS/MCLK: R1229.1, U1202.8
/DDS/MDAC_CS: U1101.40, U1204.6
/DDS/MDAC_SCK: U1101.41, U1204.4
/DDS/MDAC_SDIN: U1101.123, U1204.5
/DDS/MDAC_SDO: U1101.42, U1204.7
/DDS/~DDS_DIV10: U1213.4, U1213.5
/Ethernet/ETH_RXN: L201.8, R204.2, U202.22
/Ethernet/ETH_RXP: L201.6, R203.2, U202.23
/Ethernet/ETH_TXN: L201.3, R202.2, U202.20
/Ethernet/ETH_TXP: L201.1, R201.2, U202.21
/Ethernet/MODE0: R205.1, R217.2, U202.8
/Ethernet/MODE1: R206.1, R218.2, U202.7
/Ethernet/MODE2: R208.1, R219.2, U202.11
/Ethernet/NRST: C1105.1, J1102.10, R1104.2, U202.15, U1101.25
/Ethernet/REFCLK0: R212.1, R220.2, U202.14
/Ethernet/REF_CLK: R212.2, U1101.35
/Ethernet/RMII_CRS_DV: R208.2, U1101.43
/Ethernet/RMII_MDC: U202.13, U1101.27
/Ethernet/RMII_MDIO: R221.2, U202.12, U1101.36
/Ethernet/RMII_RXD0: R205.2, U1101.44
/Ethernet/RMII_RXD1: R206.2, U1101.45
/Ethernet/RMII_TXD0: U202.17, U1101.128
/Ethernet/RMII_TXD1: U202.18, U1101.129
/Ethernet/RMII_TXEN: U202.16, U1101.126
/I/V Converter/IRR0: R634.2, U1101.133
/I/V Converter/IRR1: U601.4, U1101.134
/I/V Converter/IRR2: U602.4, U1101.135
/I/V Converter/IRR3: U603.4, U1101.136
/I/V Converter/IRR4: U604.4, U1101.137
/MCU/EEPROM_SCL: R1110.2, U1101.81, U1103.6
/MCU/EEPROM_SDA: R1109.2, U1101.82, U1103.5
/MCU/EEPROM_WP: U1101.80, U1103.7
/MCU/MCU_DEFAULT: J1101.1, R1106.1, U1101.37
/MCU/MCU_VDDA: C1122.1, FB1101.1, U1101.32, U1101.33
/MCU/SENS_SCL: R1107.2, U1101.100, U1102.6
/MCU/SENS_SDA: R1108.2, U1101.99, U1102.1
/MCU/TCK_SWCLK: J1102.4, U1101.109
/MCU/TMS_SWDIO: J1102.2, U1101.105
/MCU/TRIG_EN: U302.2, U1101.92
/MCU/TRIG_IN: U302.4, U1101.88
/MCU/TRIG_OUT: U302.3, U1101.91
/MCU/VDIFF0: U814.4, U1101.46
/MCU/VDIFF1: U815.4, U1101.47
/MCU/VDIFF2: U809.4, U1101.48
/Trigger/EXT_TRIG_SIGN: R303.1, U301.3, U303.12
/Trigger/TRIG_OUT_EN: U301.4, U301.10, U301.13, U303.14
/Trigger/TRIG_OUT_SIGN: U301.5, U301.9, U301.12, U303.13
Earth: C211.2, C212.1, J401.A18, J401.A22, J401.C18, J401.C22, R216.1
GND: C201.2, C202.2, C203.2, C204.2, C205.2, C206.2, C207.2, C208.2, C209.2, C210.2, C212.2, C213.2, C214.2, C301.2, C302.2, C303.2, C304.2, C305.2, C401.2, C502.2, C507.2, C509.2, C510.2, C511.2, C513.2, C514.2, C515.2, C516.2, C520.2, C521.2, C522.2, C523.2, C524.2, C525.2, C526.2, C527.2, C528.2, C529.2, C530.2, C531.2, C532.2, C533.2, C603.2, C606.2, C609.2, C612.2, C613.2, C614.2, C615.2, C616.2, C617.2, C618.2, C619.2, C620.2, C621.2, C622.2, C623.2, C701.2, C702.2, C703.2, C704.2, C705.2, C804.1, C805.1, C807.2, C808.2, C809.2, C810.2, C811.2, C812.2, C813.2, C814.2, C815.2, C816.2, C817.2, C818.2, C819.2, C820.2, C821.2, C822.2, C823.2, C902.2, C903.2, C904.2, C905.2, C908.2, C909.2, C910.2, C911.2, C912.2, C913.2, C914.2, C915.2, C916.2, C917.1, C918.1, C919.1, C920.1, C921.1, C1003.1, C1005.1, C1007.2, C1008.2, C1009.2, C1010.2, C1011.2, C1012.2, C1013.2, C1014.2, C1015.2, C1016.2, C1017.2, C1018.2, C1019.2, C1101.2, C1102.2, C1103.2, C1104.2, C1105.2, C1106.2, C1107.2, C1108.2, C1109.2, C1110.2, C1111.2, C1112.2, C1113.2, C1114.2, C1115.2, C1116.2, C1117.2, C1118.2, C1119.2, C1120.2, C1121.2, C1122.2, C1202.2, C1203.1, C1204.1, C1210.2, C1211.2, C1212.2, C1213.2, C1214.2, C1215.2, C1216.2, C1217.2, C1218.2, C1219.2, C1220.2, C1221.2, C1222.2, C1223.2, C1224.2, C1225.2, C1226.2, C1227.2, C1228.2, C1229.2, D609.1, D610.2, D801.1, D803.1, D1001.1, D1002.1, D1202.2, D1203.2, D1205.1, D1206.1, J1101.2, J1102.3, J1102.5, K403.1, Q501.2, Q603.2, Q607.2, Q611.2, Q615.2, Q617.2, Q801.2, Q1201.2, R207.2, R209.1, R213.2, R214.2, R215.2, R216.2, R508.2, R510.1, R515.2, R524.2, R526.1, R529.2, R631.2, R633.2, R707.2, R708.2, R804.2, R822.2, R1003.2, R1017.2, R1105.2, R1204.1, R1209.2, R1215.2, R1219.2, R1220.2, R1224.2, R1227.2, RV801.3, RV1001.3, TP901.1, U202.25, U302.7, U303.2, U303.8, U401.8, U501.1, U501.3, U501.5, U501.8, U502.4, U504.1, U504.3, U505.1, U505.3, U505.5, U505.8, U506.7, U506.18, U506.23, U507.4, U509.1, U509.3, U601.2, U601.5, U602.2, U602.5, U603.2, U603.5, U604.2, U604.5, U605.3, U605.9, U701.4, U702.2, U702.3, U702.6, U702.7, U703.4, U801.4, U802.4, U803.4, U804.2, U805.2, U806.4, U807.4, U808.4, U809.2, U809.5, U810.2, U811.2, U812.4, U813.4, U814.2, U814.5, U815.2, U815.5, U901.1, U902.7, U904.1, U905.5, U906.1, U907.6, U908.1, U1001.4, U1002.4, U1003.2, U1004.2, U1005.4, U1006.4, U1007.2, U1007.5, U1008.2, U1009.2, U1010.4, U1011.4, U1012.2, U1012.5, U1101.16, U1101.31, U1101.38, U1101.51, U1101.61, U1101.83, U1101.94, U1101.107, U1101.120, U1101.130, U1102.2, U1103.1, U1103.2, U1103.3, U1103.4, U1202.7, U1202.9, U1202.10, U1202.11, U1202.12, U1202.17, U1202.18, U1204.2, U1204.3, U1206.9, U1206.15, U1208.2, U1208.5, U1209.3, U1210.3, U1211.2, U1211.5, U1212.3, U1212.8, U1213.8, U1214.2, U1214.5, X1201.2
GNDPWR: C901.2, C906.2, C907.2, D902.2, D903.1, J401.A27, J401.A28, J401.C27, J401.C28, U902.1, U903.4, U905.2, U907.2
GND_TRIG: C306.2, C307.2, C308.2, D301.2, D302.1, D303.2, J401.C16, R306.2, U301.1, U301.7, U303.9, U303.15
unnamed: C208.1, C209.1, U202.6
unnamed: C211.1, R210.2, R211.2
unnamed: C213.1, U202.5, Y201.2
unnamed: C214.1, U202.4, Y201.1
unnamed: C309.2, R306.1
unnamed: C501.1, R505.2, U502.1
unnamed: C501.2, R501.2, U502.2
unnamed: C502.1, R504.1, U501.7
unnamed: C503.1, R509.1, U502.3
unnamed: C503.2, R508.1, U503.2, U504.4
unnamed: C504.1, R501.1, R505.1, U506.16
unnamed: C504.2, R514.1, R517.1, U506.17
unnamed: C505.1, R511.1, U502.5
unnamed: C505.2, R515.1, U504.5
unnamed: C506.1, R514.2, U502.7
unnamed: C506.2, R517.2, U502.6
unnamed: C507.1, R516.1, U505.7
unnamed: C508.1, R519.2, U507.1
unnamed: C508.2, R518.2, U507.2
unnamed: C511.1, U506.24
unnamed: C512.1, R525.1, U507.3
unnamed: C512.2, R524.1, U508.2, U509.4
unnamed: C513.1, C514.1, R520.2
unnamed: C515.1, C516.1, R521.2
unnamed: C517.1, R518.1, R519.1, U506.21
unnamed: C517.2, R528.1, R530.1, U506.20
unnamed: C518.1, R527.1, U507.5
unnamed: C518.2, R529.1, U509.5
unnamed: C519.1, R528.2, U507.7
unnamed: C519.2, R530.2, U507.6
unnamed: C601.1, R601.2
unnamed: C601.2, Q603.3
unnamed: C602.1, Q601.1, Q602.1, R602.1
unnamed: C602.2, C605.2, C608.2, C611.2, K601.2, R601.1, R602.2, R608.1, R609.2, R615.1, R616.2, R622.1, R623.2, R629.1, R630.1, R632.2, U605.1, U605.2
unnamed: C603.1, D601.1, D602.1, Q604.3, R606.1
unnamed: C604.1, R608.2
unnamed: C604.2, Q607.3
unnamed: C605.1, Q605.1, Q606.1, R609.1
unnamed: C606.1, D603.1, D604.1, Q608.3, R613.1
unnamed: C607.1, R615.2
unnamed: C607.2, Q611.3
unnamed: C608.1, Q609.1, Q610.1, R616.1
unnamed: C609.1, D605.1, D606.1, Q612.3, R620.1
unnamed: C610.1, R622.2
unnamed: C610.2, Q615.3
unnamed: C611.1, Q613.1, Q614.1, R623.1
unnamed: C612.1, D607.1, D608.1, Q616.3, R627.1
unnamed: C613.1, R630.2
unnamed: C701.1, U701.5
unnamed: C702.1, R701.2
unnamed: C703.1, R703.1, U703.7
unnamed: C704.1, R702.2, R703.2, R704.2
unnamed: C801.1, R802.2
unnamed: C802.1, R818.2
unnamed: C803.1, R817.1, U805.1, U806.6
unnamed: C803.2, R816.1, R817.2, U806.2
unnamed: C804.2, FB801.1, R819.1
unnamed: C805.2, FB801.2, U813.7
unnamed: C806.1, R830.1, U811.1, U812.6
unnamed: C806.2, R829.1, R830.2, U812.2
unnamed: C901.1, C906.1, C907.1, D901.1, L901.1, Q901.2, U903.2, U905.1, U907.1
unnamed: C902.1, U901.3, U902.6
unnamed: C908.1, U904.3, U905.7
unnamed: C912.1, U906.3, U907.7
unnamed: C917.2, U907.5, U908.2
unnamed: C1001.1, R1001.2
unnamed: C1002.1, R1011.1, U1004.1, U1005.6
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

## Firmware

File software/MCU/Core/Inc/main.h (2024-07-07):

/* USER CODE BEGIN Header */
/**
  ******************************************************************************
  * @file           : main.h
  * @brief          : Header for main.c file.
  *                   This file contains the common defines of the application.
  ******************************************************************************
  * @attention
  *
  * <h2><center>&copy; Copyright (c) 2021 STMicroelectronics.
  * All rights reserved.</center></h2>
  *
  * This software component is licensed by ST under Ultimate Liberty license
  * SLA0044, the "License"; You may not use this file except in compliance with
  * the License. You may obtain a copy of the License at:
  *                             www.st.com/SLA0044
  *
  ******************************************************************************
  */
/* USER CODE END Header */

/* Define to prevent recursive inclusion -------------------------------------*/
#ifndef __MAIN_H
#define __MAIN_H

#ifdef __cplusplus
extern "C" {
#endif

/* Includes ------------------------------------------------------------------*/
#include "stm32h7xx_hal.h"

#include "stm32h7xx_ll_rcc.h"
#include "stm32h7xx_ll_spi.h"
#include "stm32h7xx_ll_system.h"
#include "stm32h7xx_ll_gpio.h"
#include "stm32h7xx_ll_exti.h"
#include "stm32h7xx_ll_bus.h"
#include "stm32h7xx_ll_cortex.h"
#include "stm32h7xx_ll_utils.h"
#include "stm32h7xx_ll_pwr.h"
#include "stm32h7xx_ll_dma.h"

/* Private includes ----------------------------------------------------------*/
/* USER CODE BEGIN Includes */

/* USER CODE END Includes */

/* Exported types ------------------------------------------------------------*/
/* USER CODE BEGIN ET */

/* USER CODE END ET */

/* Exported constants --------------------------------------------------------*/
/* USER CODE BEGIN EC */

/* USER CODE END EC */

/* Exported macro ------------------------------------------------------------*/
/* USER CODE BEGIN EM */

/* USER CODE END EM */

/* Exported functions prototypes ---------------------------------------------*/
void Error_Handler(void);

/* USER CODE BEGIN EFP */

/* USER CODE END EFP */

/* Private defines -----------------------------------------------------------*/
#define IDIFF0_Pin LL_GPIO_PIN_3
#define IDIFF0_GPIO_Port GPIOE
#define SPI4_NSS_Pin LL_GPIO_PIN_4
#define SPI4_NSS_GPIO_Port GPIOE
#define IDIFF1_Pin LL_GPIO_PIN_13
#define IDIFF1_GPIO_Port GPIOC
#define SPI5_NSS_Pin LL_GPIO_PIN_6
#define SPI5_NSS_GPIO_Port GPIOF
#define nRDC_Pin LL_GPIO_PIN_10
#define nRDC_GPIO_Port GPIOF
#define TRIG_EN_Pin LL_GPIO_PIN_9
#define TRIG_EN_GPIO_Port GPIOE
#define TRIG_OUT_Pin LL_GPIO_PIN_10
#define TRIG_OUT_GPIO_Port GPIOE
#define TRIG_IN_Pin LL_GPIO_PIN_11
#define TRIG_IN_GPIO_Port GPIOE
#define TRIG_IN_EXTI_IRQn EXTI15_10_IRQn
#define CXN_REL6_Pin LL_GPIO_PIN_12
#define CXN_REL6_GPIO_Port GPIOE
#define CXN_REL5_Pin LL_GPIO_PIN_13
#define CXN_REL5_GPIO_Port GPIOE
#define CXN_REL4_Pin LL_GPIO_PIN_14
#define CXN_REL4_GPIO_Port GPIOE
#define CXN_REL3_Pin LL_GPIO_PIN_15
#define CXN_REL3_GPIO_Port GPIOE
#define CXN_REL2_Pin LL_GPIO_PIN_10
#define CXN_REL2_GPIO_Port GPIOB
#define CXN_REL1_Pin LL_GPIO_PIN_11
#define CXN_REL1_GPIO_Port GPIOB
#define nADC2_RST_Pin LL_GPIO_PIN_15
#define nADC2_RST_GPIO_Port GPIOB
#define ADC2_MDIV_Pin LL_GPIO_PIN_8
#define ADC2_MDIV_GPIO_Port GPIOD
#define nADC2_HPF_Pin LL_GPIO_PIN_9
#define nADC2_HPF_GPIO_Port GPIOD
#define ADC2_M0_Pin LL_GPIO_PIN_10
#define ADC2_M0_GPIO_Port GPIOD
#define EEPROM_WP_Pin LL_GPIO_PIN_11
#define EEPROM_WP_GPIO_Port GPIOD
#define ADC2_M1_Pin LL_GPIO_PIN_14
#define ADC2_M1_GPIO_Port GPIOD
#define IRR0_Pin LL_GPIO_PIN_8
#define IRR0_GPIO_Port GPIOG
#define VDIFF0_Pin LL_GPIO_PIN_6
#define VDIFF0_GPIO_Port GPIOC
#define VDIFF2_Pin LL_GPIO_PIN_7
#define VDIFF2_GPIO_Port GPIOC
#define VDIFF1_Pin LL_GPIO_PIN_8
#define VDIFF1_GPIO_Port GPIOC
#define IRR4_Pin LL_GPIO_PIN_9
#define IRR4_GPIO_Port GPIOA
#define IRR2_Pin LL_GPIO_PIN_10
#define IRR2_GPIO_Port GPIOA
#define IRR1_Pin LL_GPIO_PIN_11
#define IRR1_GPIO_Port GPIOA
#define IRR3_Pin LL_GPIO_PIN_12
#define IRR3_GPIO_Port GPIOA
#define SPI3_NSS_Pin LL_GPIO_PIN_15
#define SPI3_NSS_GPIO_Port GPIOA
#define ADC1_RVS1_Pin LL_GPIO_PIN_0
#define ADC1_RVS1_GPIO_Port GPIOD
#define ADC1_RVS2_Pin LL_GPIO_PIN_1
#define ADC1_RVS2_GPIO_Port GPIOD
#define MCU_DEFAULT_Pin LL_GPIO_PIN_2
#define MCU_DEFAULT_GPIO_Port GPIOD
#define ADC_SEL_Pin LL_GPIO_PIN_3
#define ADC_SEL_GPIO_Port GPIOD
#define LED_BLUE_Pin LL_GPIO_PIN_7
#define LED_BLUE_GPIO_Port GPIOD
#define LED_RED_Pin LL_GPIO_PIN_9
#define LED_RED_GPIO_Port GPIOG
#define LED_GREEN_Pin LL_GPIO_PIN_10
#define LED_GREEN_GPIO_Port GPIOG
#define DDS_LPF_Pin LL_GPIO_PIN_5
#define DDS_LPF_GPIO_Port GPIOB
#define MUX_A0_Pin LL_GPIO_PIN_6
#define MUX_A0_GPIO_Port GPIOB
#define MUX_A1_Pin LL_GPIO_PIN_7
#define MUX_A1_GPIO_Port GPIOB
#define DDS_DIV8_Pin LL_GPIO_PIN_8
#define DDS_DIV8_GPIO_Port GPIOB
#define DDS_DIV4_Pin LL_GPIO_PIN_9
#define DDS_DIV4_GPIO_Port GPIOB
#define DDS_DIV2_Pin LL_GPIO_PIN_0
#define DDS_DIV2_GPIO_Port GPIOE
#define nDDS_DIV10_Pin LL_GPIO_PIN_1
#define nDDS_DIV10_GPIO_Port GPIOE

/* USER CODE BEGIN Private defines */

/* USER CODE END Private defines */

#ifdef __cplusplus
}
#endif

#endif /* __MAIN_H */

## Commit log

2021-04-30 Star of the project
    [ADC.sch, Connector.sch, ETH1CLCR2.kicad_pcb, ETH1CLCR2.sch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]
2021-04-30 Project based on https://hackaday.io/project/165409-precision-impedance-meter-asdflcr1
    [ADC.sch, Connector.sch, ETH1CLCR2.sch, Ethernet.sch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]
2021-05-01 Schematic design
    [ADC.sch, Connector.sch, ETH1CLCR2.sch, Ethernet.sch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]
2021-05-02 Footprints assigned.
    [ADC.sch, Connector.sch, ETH1CLCR2.kicad_pcb, ETH1CLCR2.sch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]
2021-05-02 PCB layout
    [ETH1CLCR2.kicad_pcb, ETH1CLCR2.sch, IV_Converter.sch, Power.sch]
2021-05-06 Modification of the function generator schematic.
    [ADC.sch, Connector.sch, ETH1CLCR2.kicad_pcb, ETH1CLCR2.sch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]
2021-05-25 Modification in schematic and PCB
    [DDS.sch, ETH1CLCR2.sch, MCU.sch]
2021-05-29 Fixed PCB file
    [ADC.sch, Clock.sch, Connector.sch, DDS.sch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]
2021-06-02 Schematic and PCB modifications
    [ADC.sch, I_Diff_Amp.sch, V_Diff_Amp.sch]
2021-06-03 Fixed folders. Fixes in schematics.
    [ADC.sch, Clock.sch, Connector.sch, DDS.sch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]
2021-06-03 PCB done
    [Connector.sch, DDS.sch, ETH1CLCR2.csv, ETH1CLCR2.ods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]
2021-11-12 Ethernet connection and SCPI commands are working. Swapped red and green LED in the schematic.
    [MCU.sch]
2021-11-15 Fixed bug with not switching pin but port. EEPROM and SPI3 works correctly.
2022-01-28 Converter hardware files to Kicad 6
    [ADC.kicad_sch, Connector.kicad_sch, DDS.kicad_sch, ETH1CLCR2.kicad_sch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]
2022-02-20 DAC7811 and DG409 work. The STM32CUBE sets the TICK_INIT_PRIORITY to 15, this is invalid for FreeRTOS, should be 0 (need to change stm32h7xx_hal_conf.h after new code generation).
2022-02-20 Added text to schematics, software development.
    [DDS.kicad_sch, I_Diff_Amp.kicad_sch, V_Diff_Amp.kicad_sch]
2022-03-13 Software development and added comments to the schematics.
    [ADC.kicad_sch, DDS.kicad_sch, IV_Converter.kicad_sch]
2022-04-12 Software development
    [ADC.kicad_sch, Connector.kicad_sch, ETH1CLCR2.kicad_sch, Trigger.kicad_sch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]
2023-03-04 Converted HW files to KiCAD 7.0.
    [ADC.kicad_sch, Connector.kicad_sch, DDS.kicad_sch, ETH1CLCR2.kicad_sch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]
2024-07-07 Project updated
    [ADC.kicad_sch, Connector.kicad_sch, DDS.kicad_sch, ETH1CLCR2.kicad_sch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]
